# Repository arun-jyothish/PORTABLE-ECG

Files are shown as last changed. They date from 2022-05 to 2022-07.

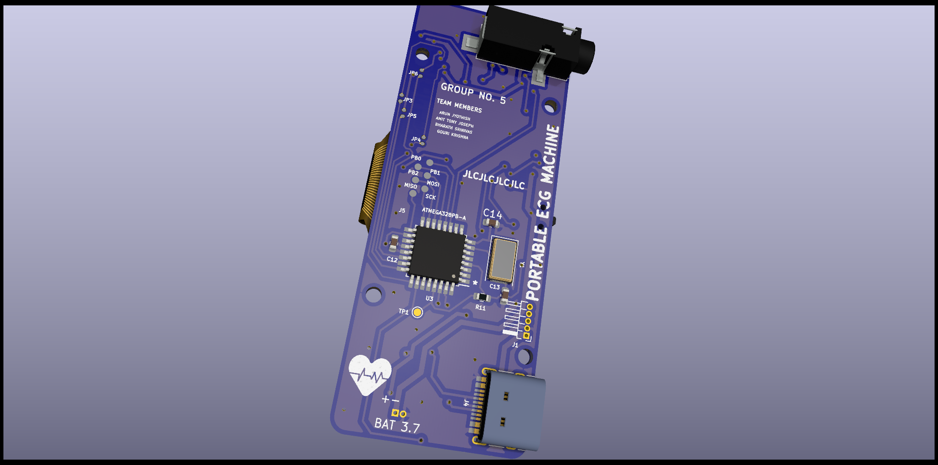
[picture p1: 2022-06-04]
KICAD FILES/imgs/P-ECG rev 3 kicad render 9.png

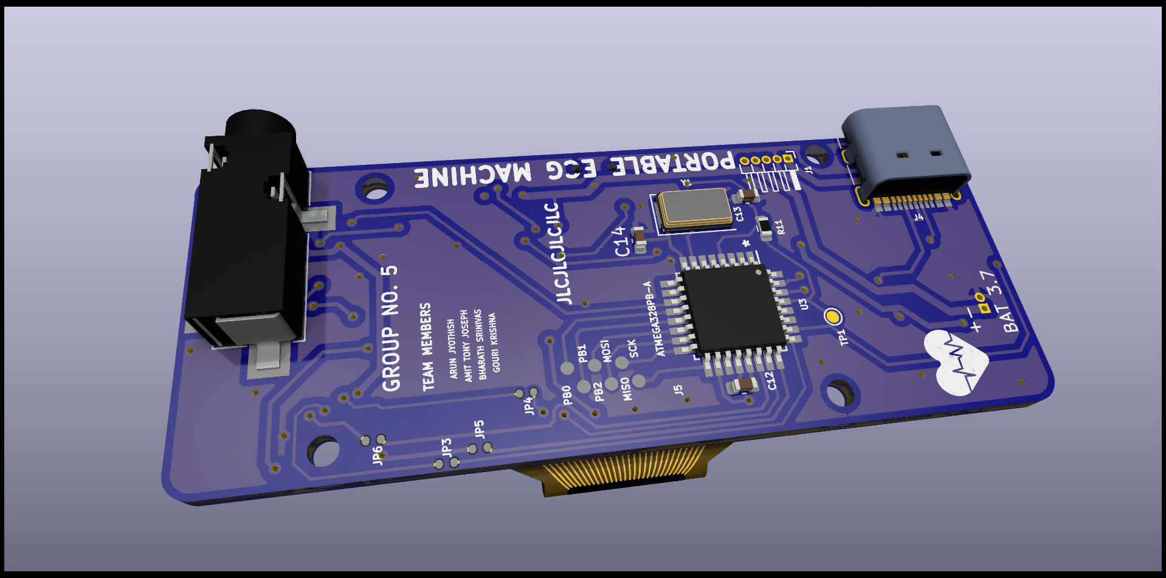
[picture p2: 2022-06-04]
KICAD FILES/imgs/P-ECG rev 3 kicad render 8.png

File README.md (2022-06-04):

# PORTABLE-ECG
A Handheld ECG Machine with Mobile phone and Laptop interface. Cardiac condition prediction using ML

[jump to README 2](src/README.md)

[variable link][var link]
LOCK

[var link]: https://GOOGLE.COM 

|part name|LCSC PART NO|LINK|
|-----|-----|----|
|OLED| 	C2890600|https://lcsc.com/product-detail/span-style-background-color-ff0-OLED-span-Displays-Modules_Shenzhen-Allvision-Tech-N096-2864TMBEG0-H30_C2890600.html|
|RESISTOR|
|CAPACITOR|
|TYPEC CONN|
hello world
<br>

[][Contributors-url]

<br>

f3d render 1 

## P-ECG MACHINE

In the prediction feature, patient's ECG signal is compared with various cardio gram.
as the processing result the machine filter out many heart disease and predicts the most probable disease that should affect the person's life'

## BLOCK DIAGRAM
~~~mermaid

graph TD
 
    UART-->PWR
    PWR[USB PORT]-->CHR[CHARGING CIRCUIT]
    CHR-->BAT[BATTERY 3.7 LI-ION]
    RGL[POWER REGULATOR]-.->|3.3 VOLT|OLED[OLED 128*64]
    CHR-->RGL
    BAT-->RGL
    RGL-.->|3.7 VOLT|UC 
    UC{MICROCONTROLLER}-->OLED
   
    UC-->UART[USB TO TTL CONVERTER]
    PWR-.->EXT[COMPUTER]
    PWR-.->EXT2[MOBILE]
    probe[/PROBE/]-->|DATA|INS
    RGL-.->INS
    RA((RA))-->probe
    RL((RL))-->probe
    LA((LA))-->probe
    INS[INSTRUMENTATION AMPLIFIER] --->|ANALOG DATA| UC
~~~

~~~mermaid
graph TD 

   I((IDEATION)) --> Q[PREPARE FAQ] 
    I --> D[CONSTRAINTS IN NEW IMPLEMENTATION]
    D-->M[ MEASURES TAKEN ]
    EX[IDENTIFYING EXISTING TECHNOLOGY]-->I
    FL[IDENTIFYING LIMITATIONS]-->I
    
~~~
~~~mermaid
graph TD
    H[COMPONENTS SELECTION]-->SCH[PREPARE SCHEMATICS]
    SCH-->PCB[DESIGN PCB LAYOUT]
   DSN[CHASY DESIGN]-->TST[TESTING STAGE]
    TST-.->|FAIL|SCH
    TST==>|SUCCESS|FINAL((PRODUCT))
    PCB-->DSN

~~~
[contributors-shield]: https://img.shields.io/github/contributors/Arun-jyothish/PORTABLE-ECG.svg?style=for-the-badge
[Contributors-url]:https://github.com/Arun-jyothish/PORTABLE-ECG/network/members

~~~mermaid

~~~

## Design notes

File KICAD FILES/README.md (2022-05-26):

# PORTABLE ECG MACHINE

According to current statistics, over 1.6 million people die in India due to a lack of access to
health care. Most of these cases occur in rural areas of the developing nations including India.<br>
Difficulty in accessing immediate health care is important for the proper treatment and recovery
of many diseases.
<br>
Heart diseases come under a category of conditions that need to be detected early for proper
recovery and treatment.

**An Electrocardiogram (ECG)** is a simple test that can be used to detect
the heart’s rhythm and electrical activity, thereby diagnosing conditions that affect the heart.

 <br>
It
can be used to investigate the symptoms of possible heart disease including chest pain,
palpitations, dizziness, shortness of breath, etc... which may point toward any heart condition
including 

<br>

* tachycardia
* bradycardia
* and heart attack.

<br>
There are many high-grade types of equipment in hospitals to carry out ECGs on patients. But in
many cases, the time taken to reach a hospital might be the fate that decides life or death. <br>There
are many places in the world where people are unable to access healthcare services quickly. <br>In
such cases, mainly in rural areas, a portable handheld device to carry out resting ECG can be
useful in detecting a heart condition.

<br>

### COMPONENTS USED

|HARDWARE|SOFTWARE|CHASE|
|--------|--------|-----|
|INSTRUMENTATION AMPLIFIER|STM32 CUBE IDE| PLA|

````mermaid
graph TD 
   I((IDEATION)) --> Q[PREPARE FAQ] 
    I --> D[CONSTRAINTS IN NEW IMPLEMENTATION]
    D-->M[ MEASURES TAKEN ]
    EX[IDENTIFYING EXISTING TECHNOLOGY]-->I
    FL[IDENTIFYING LIMITATIONS]-->I

````

--------

## HARDWARE IMPLEMENTATION STEPS

````mermaid
graph TD
    H[COMPONENTS SELECTION]-->SCH[PREPARE SCHEMATICS]
    SCH-->PCB[DESIGN PCB LAYOUT]
   DSN[CHASY DESIGN]-->TST[TESTING STAGE]
    TST-.->|FAIL|SCH
    TST==>|SUCCESS|FINAL((PRODUCT))
    PCB-->DSN
````

## SYSTEM SPECIFICATION

* HEART RATE MEASUREMENT
* SPO2 MEASURE
* PLOT/STORE ECG IN MOBILE DEVICES
* DETECT CARDIAC VARIATION DUE TO COMMONLY KNOWN HEART DISEASE

## GANT CHART

~~~mermaid

~~~

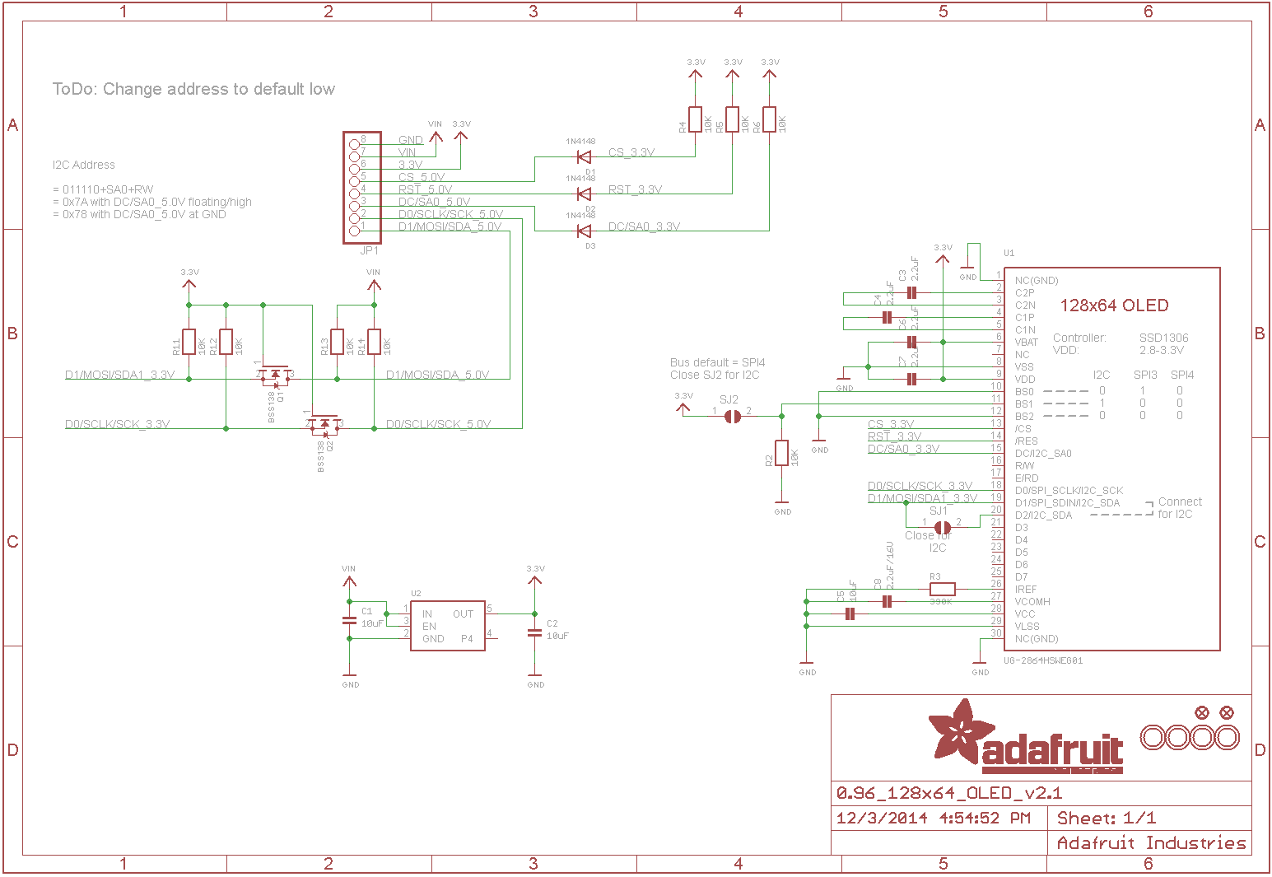
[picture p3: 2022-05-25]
imgs/oled_adafruit_0.94inch_12864_v2.1_schematics.png.png

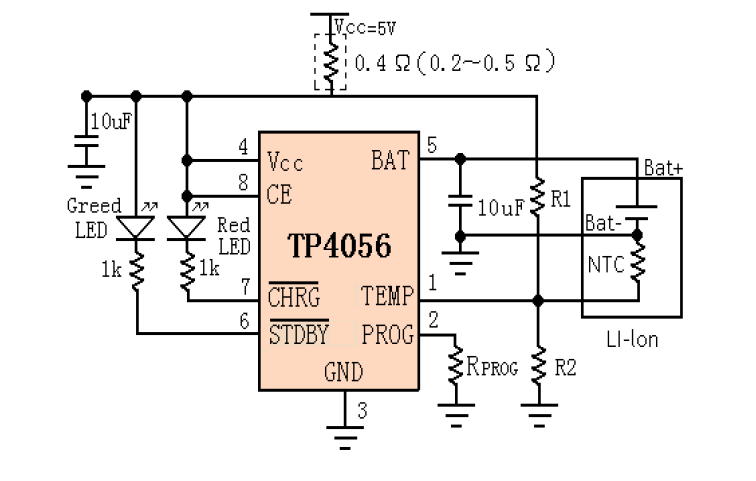
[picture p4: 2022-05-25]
imgs/TP4056 SCHEMATICS.png

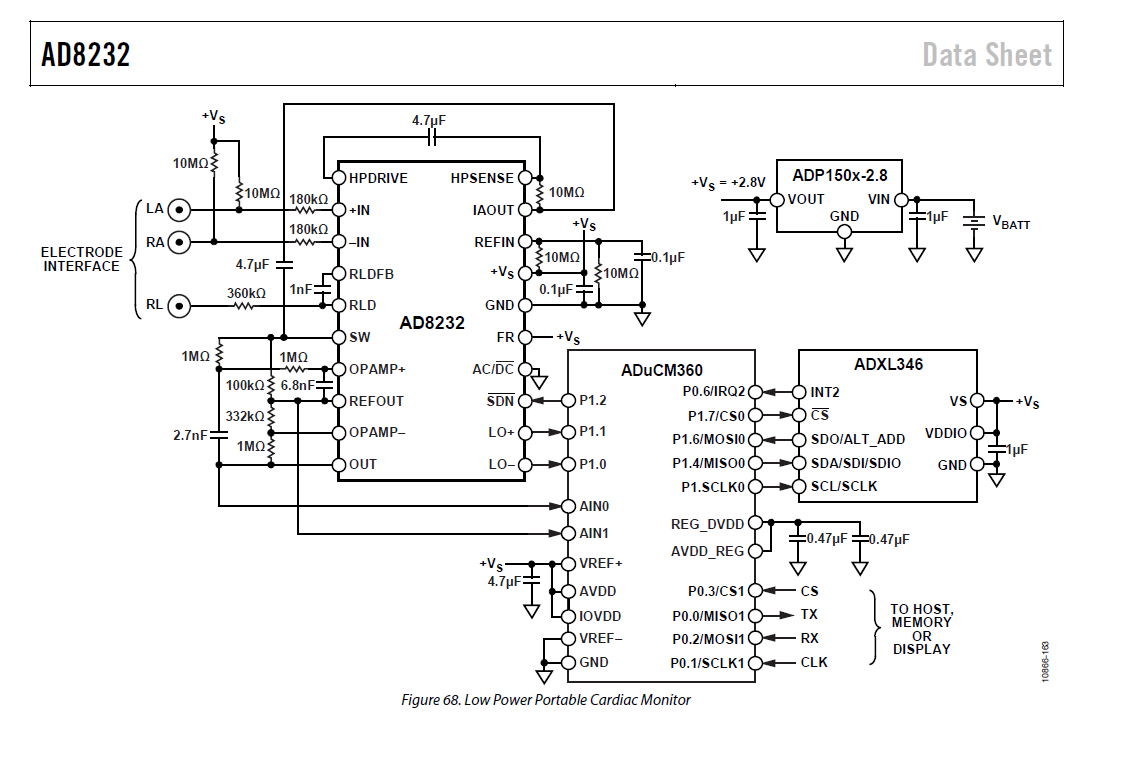
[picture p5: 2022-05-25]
imgs/AD8232 REF SCHEMATICS.png

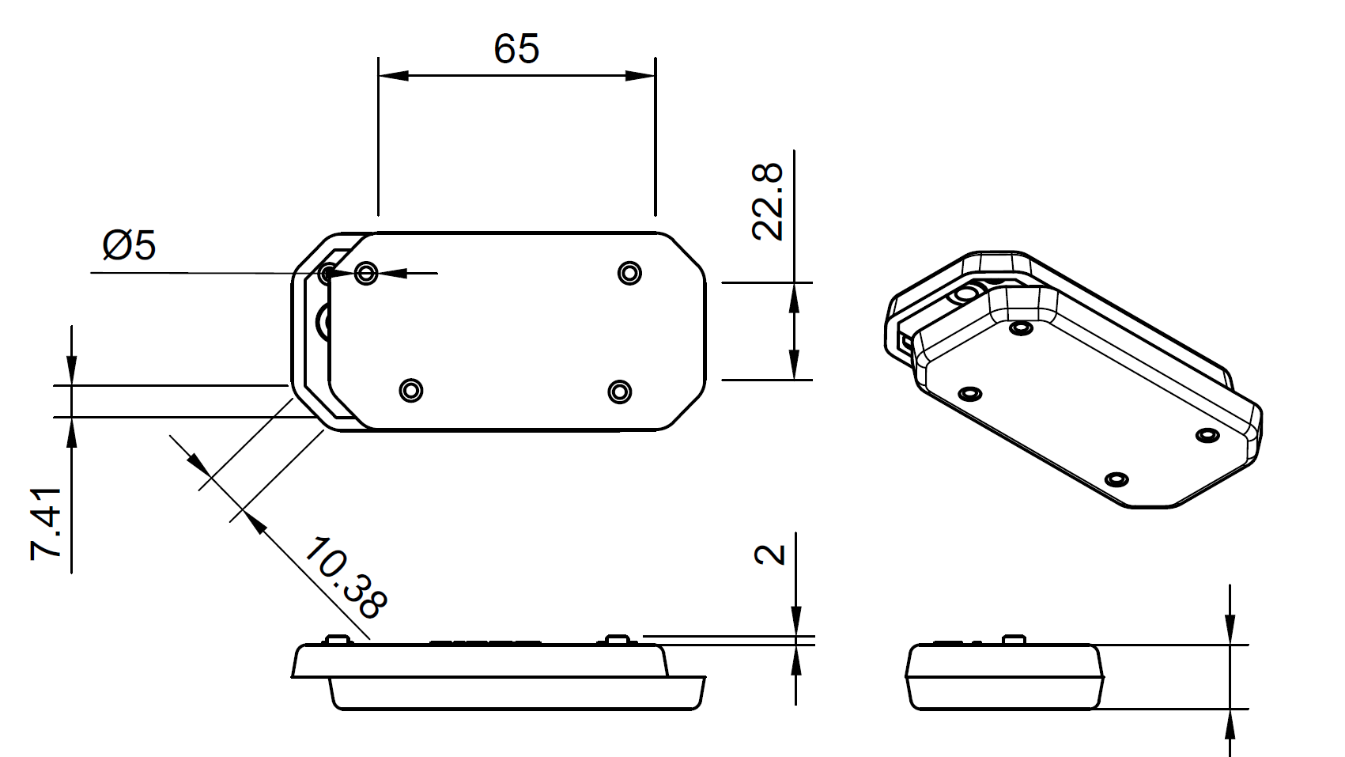
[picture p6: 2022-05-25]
imgs/DRAWING ENCLOSURE.png

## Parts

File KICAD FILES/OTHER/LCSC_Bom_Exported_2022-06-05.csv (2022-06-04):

LCSC Part Number | Package | Value | Quoted Manufacturer | Quoted LCSC Part Number | Quantity | Unit Price | Order Price | Quantity Available | Min\Mult Order Qty | RoHS | Part Match Confidence
C2204347 | Capacitor_SMD:C_0603_1608Metric | 4.7uf | AVX | C2204347 | 1 |  | 0.01 |  | 1\1 | yes | 100%
C2184695 | Capacitor_SMD:C_0603_1608Metric | 10p | KEMET | C2184695 | 1 |  | 0.01 |  | 1\1 | yes | 100%
C100040 | Capacitor_SMD:C_0603_1608Metric | 1nf | YAGEO | C100040 | 100 | 0.0026 | 0.26 | 8197500 | 100\100 | yes | 100%
C107085 | Capacitor_SMD:C_0603_1608Metric | 2.7nf | YAGEO | C107085 | 100 | 0.0036 | 0.36 | 1100 | 100\100 | yes | 100%
C2185892 | Capacitor_SMD:C_0603_1608Metric | 6.8nf | Vishay Intertech | C2185892 | 1 |  | 0.01 |  | 1\1 | yes | 100%
C2237744 | Capacitor_SMD:C_0603_1608Metric | .1uf | AVX | C2237744 | 1 |  | 0 |  | 1\1 | yes | 100%
C2168630 | Capacitor_SMD:C_0603_1608Metric | 1uf | KEMET | C2168630 | 1 |  | 0.01 |  | 1\1 | yes | 100%
C2858007 | Capacitor_SMD:C_0603_1608Metric | 2.2uf | Kyocera | C2858007 | 1 |  | 0.01 |  | 1\1 | yes | 100%
C2167337 | Capacitor_SMD:C_0603_1608Metric | 10uf | AVX | C2167337 | 1 |  | 0.01 |  | 1\1 | yes | 100%
C109002 | Diode_SMD:D_0603_1608Metric | 4148 | LIZ Elec | C109002 | 20 |  | 0.48 |  | 20\20 | yes | 100%
C143772 | Diode_SMD:D_0603_1608Metric | D_Schottky | AVX | C143772 | 5 | 0.1088 | 0.54 | 2740 | 5\5 | yes | 100%
C221856 | tactile switch:SW_PTS525SM15SMTR2LFS | PTS525SM15SMTR2LFS | C&K | C221856 | 1 | 0.1383 | 0.14 | 6655 | 1\1 | yes | 100%
C2917809 | LED_SMD:LED_0603_1608Metric | LED GREEN | PARALIGHT | C2917809 | 10 | 0.045 | 0.45 | 3760 | 10\10 | yes | 100%
C652575 | KiCad:QFN50P400X400X80-21N-D | AD8232ACPZ | Analog Devices | C652575 | 1 |  | 3.29 |  | 1\1 | yes | 100%
C2939151 | Connector_Audio:Jack_3.5mm_CUI_SJ-3524-SMT_Horizontal | ECG PROBE | HOOYA | C2939151 | 1 | 0.1687 | 0.17 | 494 | 1\1 | yes | 100%
C2927026 | Connector_USB:USB_C_Receptacle_HRO_TYPE-C-31-M-12 | USB_C_Receptacle_USB2.0 | DEALON | C2927026 | 10 | 0.046 | 0.46 | 6380 | 10\10 | yes | 100%
C549757 | Package_TO_SOT_SMD:SOT-23 | BSS138 | Nexperia | C549757 | 1 |  | 0.3 |  | 1\1 | yes | 100%
C2907166 | Resistor_SMD:R_0603_1608Metric | 4.7k | FOJAN | C2907166 | 100 | 0.0009 | 0.09 | 95000 | 100\100 | yes | 100%
C2907090 | Resistor_SMD:R_0603_1608Metric | 180k | FOJAN | C2907090 | 100 | 0.0009 | 0.09 | 32000 | 100\100 | yes | 100%
C2907090 | Resistor_SMD:R_0603_1608Metric | 360k | FOJAN | C2907090 | 100 | 0.0009 | 0.09 | 32000 | 100\100 | yes | 100%
C2907115 | Resistor_SMD:R_0603_1608Metric | 1M | FOJAN | C2907115 | 100 | 0.001 | 0.1 | 34400 | 100\100 | yes | 100%
C2930027 | Resistor_SMD:R_0603_1608Metric | 10k | FOJAN | C2930027 | 100 | 0.0009 | 0.09 | 1457500 | 100\100 | yes | 100%
C2907151 | Resistor_SMD:R_0603_1608Metric | 330k | FOJAN | C2907151 | 100 | 0.001 | 0.1 | 56400 | 100\100 | yes | 100%
C328419 | Resistor_SMD:R_0603_1608Metric | 100k | Resistor.Today | C328419 | 10 | 0.073 | 0.73 | 25140 | 10\10 | yes | 100%
C2907088 | Resistor_SMD:R_0603_1608Metric | 0.4R | FOJAN | C2907088 | 100 | 0.0009 | 0.09 | 394400 | 100\100 | yes | 100%
C2913953 | Resistor_SMD:R_0603_1608Metric | 1k | SANYEAR | C2913953 | 20 | 0.0247 | 0.49 | 1100 | 20\20 | yes | 100%
C304747 | Resistor_SMD:R_0603_1608Metric | 390k | FH(Guangdong Fenghua Advanced Tech) | C304747 | 100 | 0.001 | 0.1 | 8100 | 100\100 | yes | 100%
C2907090 | Resistor_SMD:R_0603_1608Metric | 10M | FOJAN | C2907090 | 100 | 0.0009 | 0.09 | 32000 | 100\100 | yes | 100%
C2917808 | LED_SMD:LED_0603_1608Metric | LED RED | PARALIGHT | C2917808 | 10 | 0.045 | 0.45 | 2470 | 10\10 | yes | 100%
C2890358 | Button_Switch_SMD:SW_SPDT_PCM12 | SW_SPDT | G-Switch | C2890358 | 5 | 0.1077 | 0.54 | 20420 | 5\5 | yes | 100%
C6568 | CP2102-GM:QFN50P500X500X100-29N | CP2102-GM | SILICON LABS | C6568 | 1 | 2.6833 | 2.68 | 21873 | 1\1 | yes | 100%
C194192 | Package_QFP:TQFP-32_7x7mm_P0.8mm | ATmega328PB-A | Microchip Tech | C194192 | 1 |  | 2.88 |  | 1\1 | yes | 100%
C140319 | Package_TO_SOT_SMD:SOT-223 | LM3940IMP-3.3/NOPB | Texas Instruments | C140319 | 1 | 1.4084 | 1.41 | 1672 | 1\1 | yes | 100%
C725790 | tp4056 ftprnt:SOP127P600X175-9N | TP4056 | UMW(Youtai Semiconductor Co., Ltd.) | C725790 | 1 | 0.1348 | 0.13 | 23205 | 1\1 | yes | 100%
C2890600 | Display:OLED-128O064D | SSD1306 | Shenzhen Allvision Tech | C2890600 | 1 | 3.4696 | 3.47 | 53 | 1\1 | yes | 100%
C112972 | Crystal:Crystal_SMD_0603-2Pin_6.0x3.5mm | 16MHZ | Yangxing Tech | C112972 | 5 | 0.0904 | 0.45 | 13570 | 5\5 | yes | 100%

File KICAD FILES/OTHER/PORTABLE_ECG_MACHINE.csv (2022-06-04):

Comment | Designator | Footprint | LCSC
B-TEMP | B_TEMP1 | TestPoint:TestPoint_Pad_D1.0mm
4.7uf | C1,C15,C17,C24 | Capacitor_SMD:C_0603_1608Metric | C2204347
10p | C13,C14 | Capacitor_SMD:C_0603_1608Metric | C2184695
1nf | C16 | Capacitor_SMD:C_0603_1608Metric | C100040
2.7nf | C18 | Capacitor_SMD:C_0603_1608Metric | C107085
6.8nf | C19 | Capacitor_SMD:C_0603_1608Metric | C2185892
.1uf | C2,C8,C10,C11,C12,C22 | Capacitor_SMD:C_0603_1608Metric | C2237744
1uf | C3,C4,C5,C20,C21 | Capacitor_SMD:C_0603_1608Metric | C2168630
2.2uf | C6 | Capacitor_SMD:C_0603_1608Metric | C2858007
10uf | C7,C23 | Capacitor_SMD:C_0603_1608Metric | C2167337
D+ | D+1 | TestPoint:TestPoint_Pad_D1.0mm
D- | D-1 | TestPoint:TestPoint_Pad_D1.0mm
4148 | D1 | Diode_SMD:D_0603_1608Metric | C109002
D_Schottky | D2,D3 | Diode_SMD:D_0603_1608Metric | C143772
PTS525SM15SMTR2LFS | DRIVE1,SELECT1 | tactile switch:SW_PTS525SM15SMTR2LFS | C221856
LED GREEN | GREEN1 | LED_SMD:LED_0603_1608Metric | C2917809
AD8232ACPZ | IC1 | KiCad:QFN50P400X400X80-21N-D | C652575
UART | J1 | Connector_PinHeader_1.00mm:PinHeader_1x05_P1.00mm_Horizontal
ECG PROBE | J2 | Connector_Audio:Jack_3.5mm_CUI_SJ-3524-SMT_Horizontal | C2939151
Li-Ion 3.7 CONN | J3 | Connector_PinHeader_1.00mm:PinHeader_1x02_P1.00mm_Horizontal
USB_C_Receptacle_USB2.0 | J4 | Connector_USB:USB_C_Receptacle_HRO_TYPE-C-31-M-12 | C2927026
Conn_01x06_Male | J5 | TEST_POINT_MATRIX_6-PIN:6PIN_CONN
SolderJumper_3_Open | JP1,JP2 | TEST_POINT_MATRIX_6-PIN:3_PIN_SOLDER_JUMPER_SMD
LDO+ | JP3,JP6 | TEST_POINT_MATRIX_6-PIN:2_PIN_SMD_SOLDER_JUMPER
LDO- | JP4 | TEST_POINT_MATRIX_6-PIN:2_PIN_SMD_SOLDER_JUMPER
OUT | JP5 | TEST_POINT_MATRIX_6-PIN:2_PIN_SMD_SOLDER_JUMPER
REF | JP7 | TEST_POINT_MATRIX_6-PIN:2_PIN_SMD_SOLDER_JUMPER
RST | JP8 | TEST_POINT_MATRIX_6-PIN:2_PIN_SMD_SOLDER_JUMPER
LA | LA1 | TestPoint:TestPoint_Pad_D1.0mm
BSS138 | Q1,Q2 | Package_TO_SOT_SMD:SOT-23 | C549757
4.7k | R1 | Resistor_SMD:R_0603_1608Metric | C2907166
180k | R14,R15 | Resistor_SMD:R_0603_1608Metric | C2907090
360k | R16 | Resistor_SMD:R_0603_1608Metric | C2907090
1M | R19 | Resistor_SMD:R_0603_1608Metric | C2907115
10k | R2,R3,R5,R6,R7,R11 | Resistor_SMD:R_0603_1608Metric | C2930027
330k | R20 | Resistor_SMD:R_0603_1608Metric | C2907151
100k | R21 | Resistor_SMD:R_0603_1608Metric | C328419
0.4R | R22 | Resistor_SMD:R_0603_1608Metric | C2907088
1k | R23,R24 | Resistor_SMD:R_0603_1608Metric | C2913953
R_Small_US | R25,R26 | Resistor_SMD:R_0603_1608Metric
R_prog | R27 | Resistor_SMD:R_0603_1608Metric
390k | R4 | Resistor_SMD:R_0603_1608Metric | C304747
10M | R8,R9,R10,R12,R13,R17,R18 | Resistor_SMD:R_0603_1608Metric | C2907090
RA | RA1 | TestPoint:TestPoint_Pad_D1.0mm
LED RED | RED1 | LED_SMD:LED_0603_1608Metric | C2917808
RL | RL1 | TestPoint:TestPoint_Pad_D1.0mm
0-RST | RST_CP1 | TestPoint:TestPoint_Pad_D1.0mm
SW_SPDT | SW1 | Button_Switch_SMD:SW_SPDT_PCM12 | C2890358
AT_RST# | TP1 | TestPoint:TestPoint_Pad_D1.0mm
CP2102-GM | U2 | CP2102-GM:QFN50P500X500X100-29N | C6568
ATmega328PB-A | U3 | Package_QFP:TQFP-32_7x7mm_P0.8mm | C194192
LM3940IMP-3.3/NOPB | U4 | Package_TO_SOT_SMD:SOT-223 | C140319
TP4056 | U5 | tp4056 ftprnt:SOP127P600X175-9N | C725790
SSD1306 | U6 | Display:OLED-128O064D | C2890600
16MHZ | Y1 | Crystal:Crystal_SMD_0603-2Pin_6.0x3.5mm | C112972

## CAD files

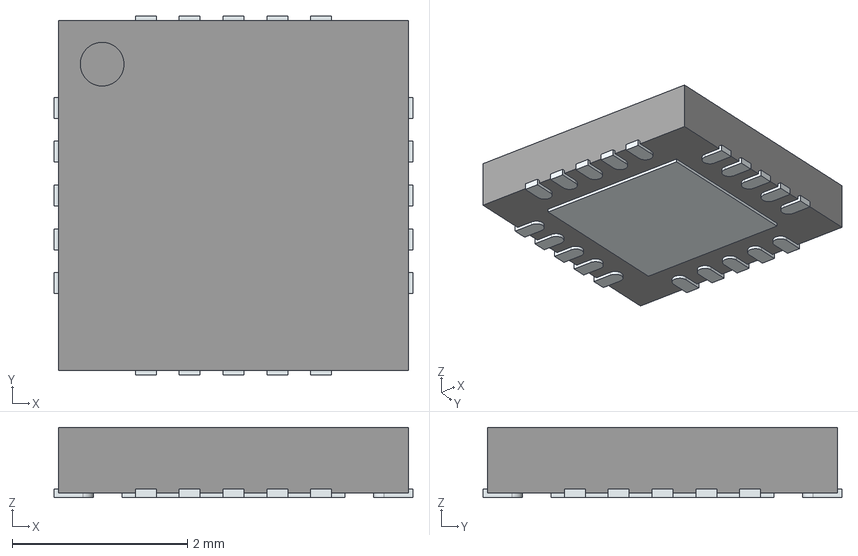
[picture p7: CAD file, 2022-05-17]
KICAD FILES/models/AD8232ACPZ/3D/AD8232ACPZ.stp
4.10 x 4.10 x 0.8 mm
ThermalPin
PinsArrayLR
PinsArrayTB

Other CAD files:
KICAD FILES/models/AD8232ACPZ/3D/AD8232ACPZ.stl

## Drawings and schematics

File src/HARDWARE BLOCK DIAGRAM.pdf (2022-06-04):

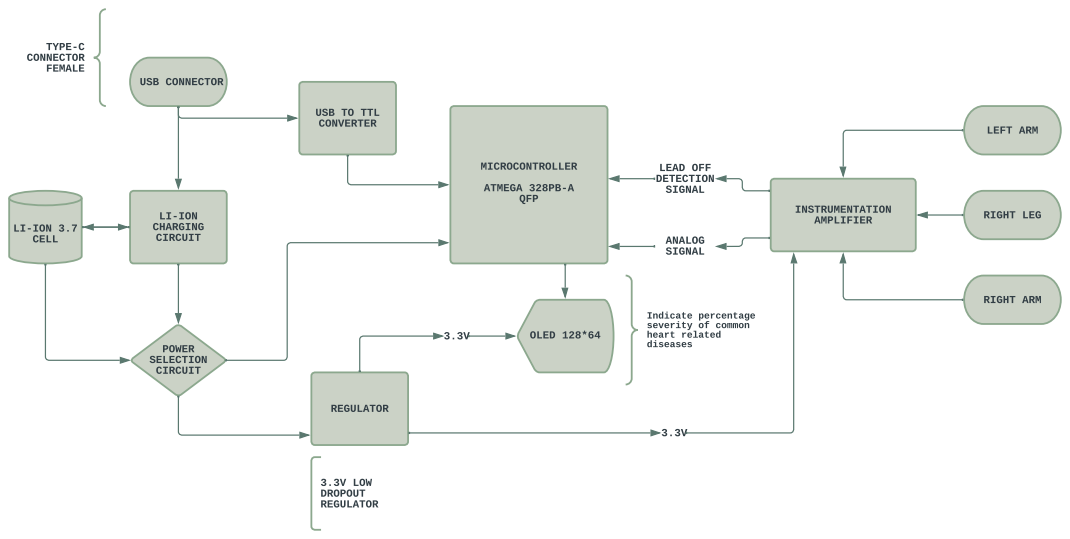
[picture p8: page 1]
MI CROCONTROLLER; ATMEGA 328PB- A QFP; USB CONNECTOR; LI - I ON CHARGI NG CI RCUI T; POWER SELECTI ON CI RCUI T; LI - I ON 3. 7 CELL; OLED 128* 64; LEFT ARM; REGULATOR; TYPE- C CONNECTOR FEMALE; 3. 3V LOW DROPOUT REGULATOR; ANALOG SI GNAL; LEAD OFF DETECTI ON SI GNAL

USB TO TTL
CONVERTER

I NSTRUMENTATI ON
AMPLI FI ER

RI GHT LEG

RI GHT ARM

I ndi cat e per cent age
sever i t y of common
hear t r el at ed
di seases

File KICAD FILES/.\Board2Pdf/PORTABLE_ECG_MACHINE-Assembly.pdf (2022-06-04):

13.2080 mm

1 | 2 | 3 | 4

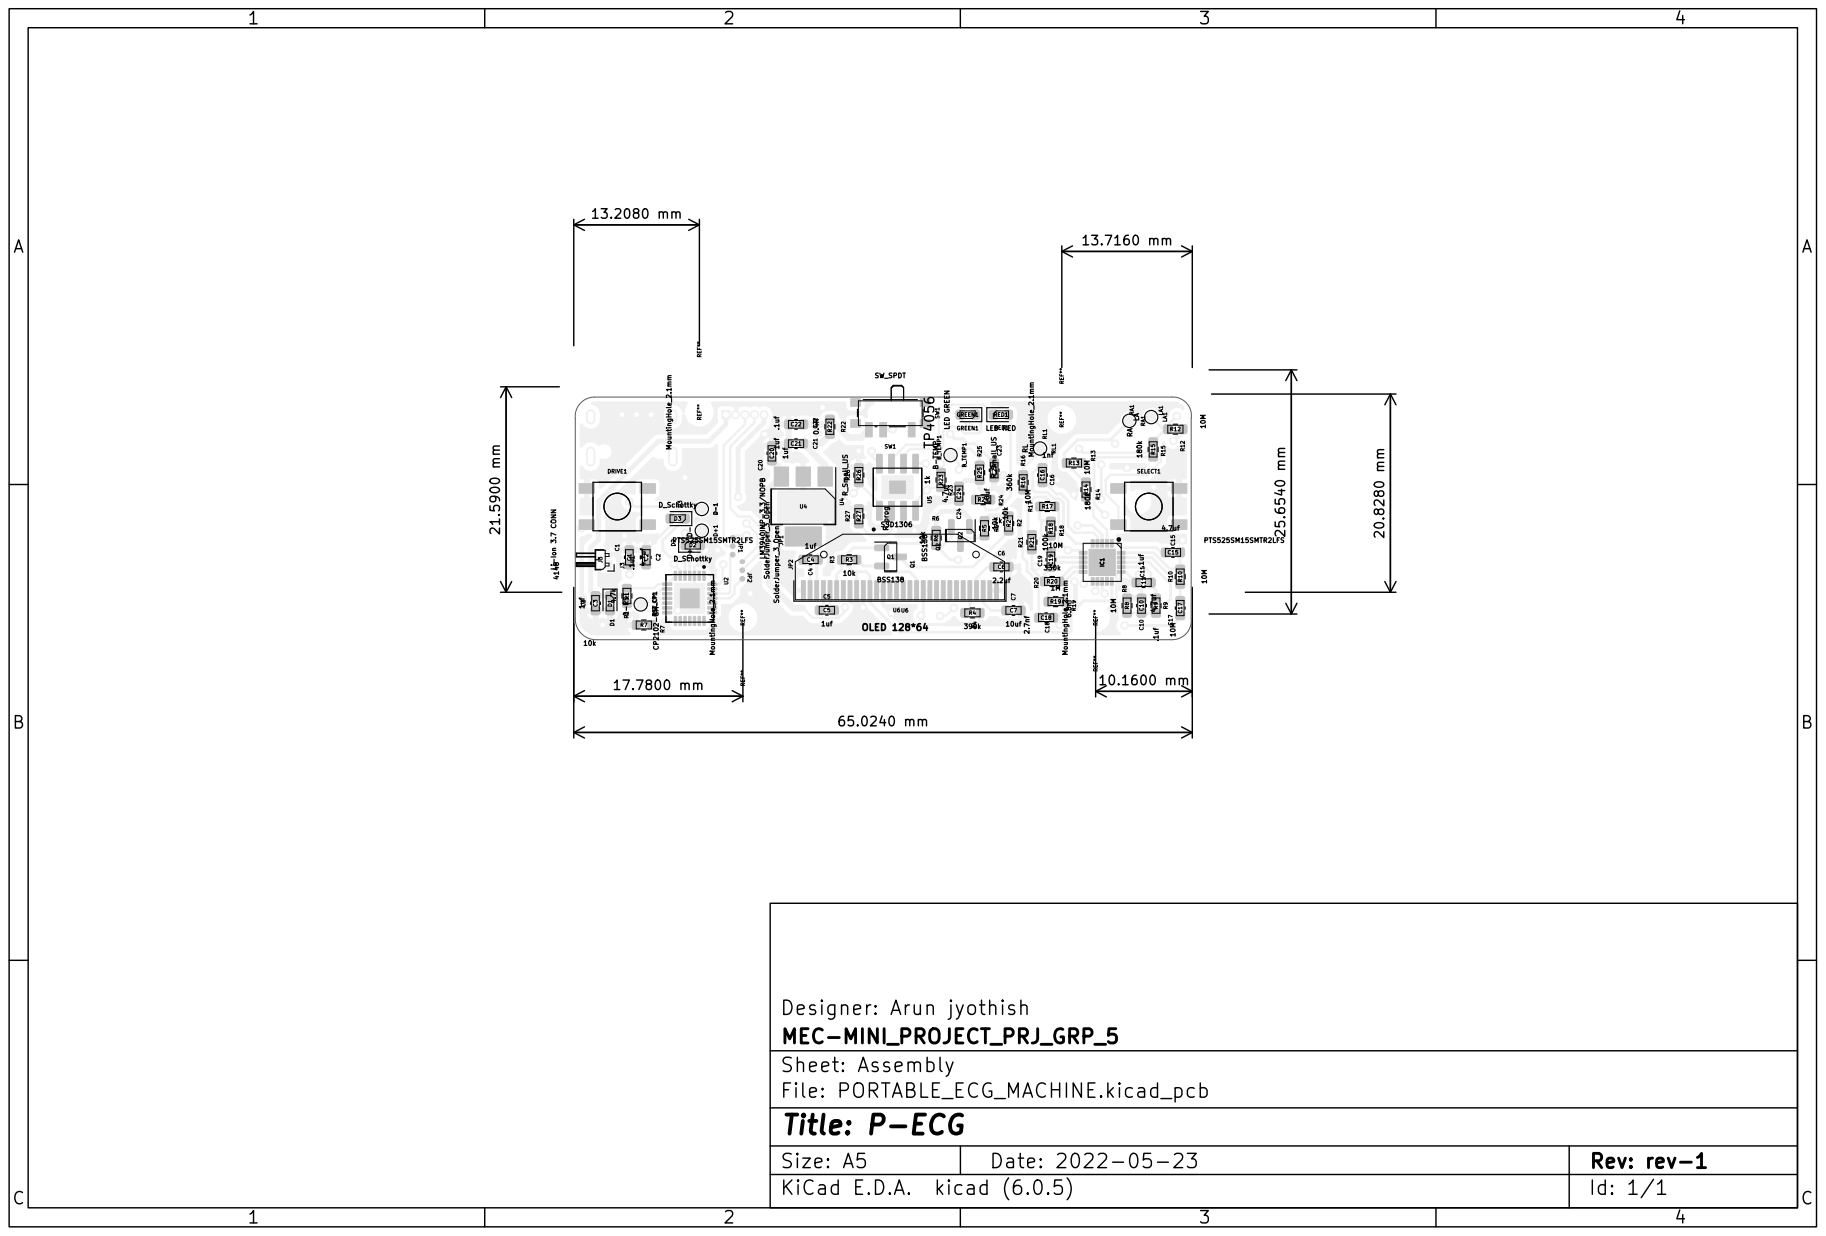
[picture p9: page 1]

J2 | TP1 1 | 2 | 3 | 4

A

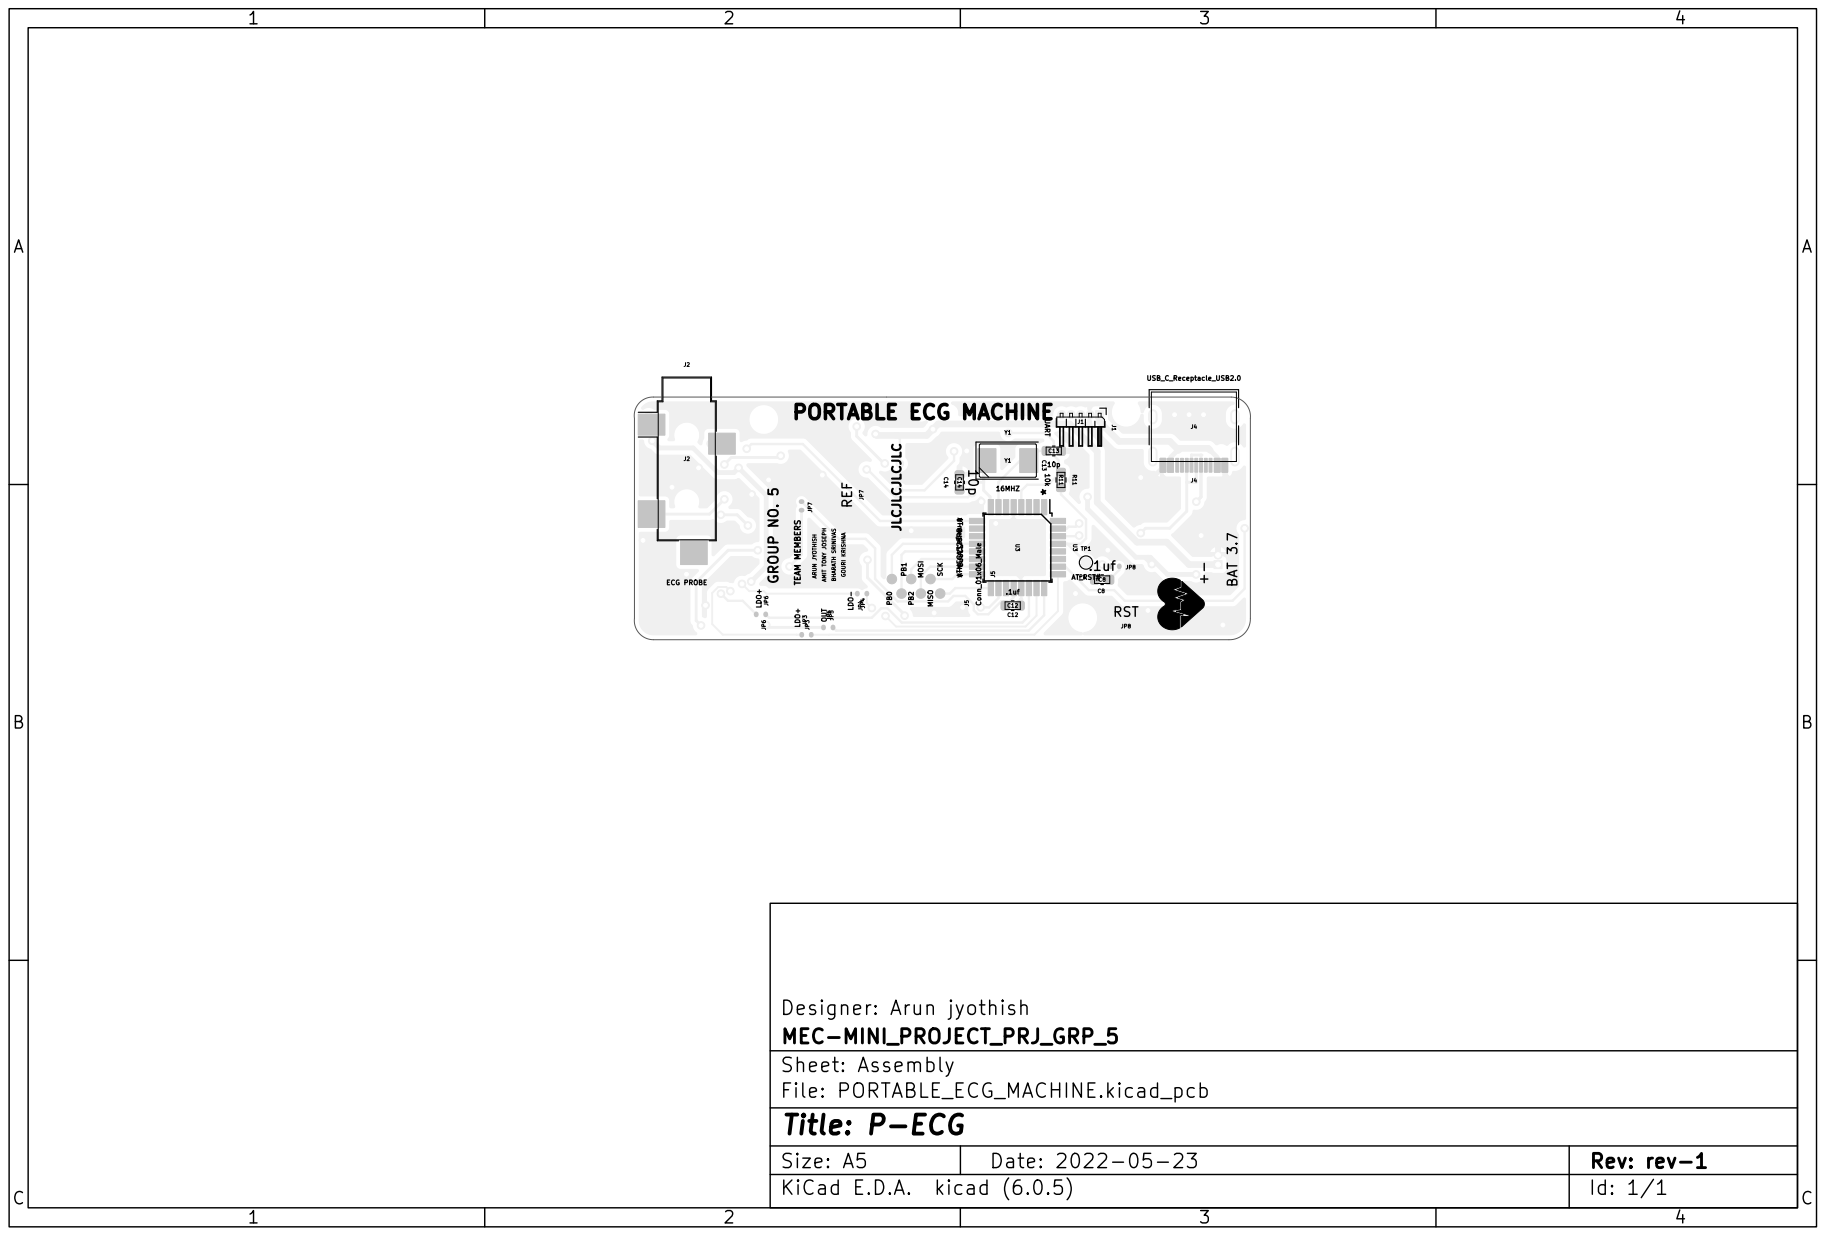
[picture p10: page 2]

PB0 GROUP NO. 5 + PB2 JLCJLCJLCJLC TEAM MEMBERS BAT 3.7 GOURI KRISHNA ATMEGA328PB-A - ARUN JYOTHISH MOSI AMIT TONY JOSEPH PB1 SCK BHARATH SRINIVAS PORTABLE ECG MACHINE MISO

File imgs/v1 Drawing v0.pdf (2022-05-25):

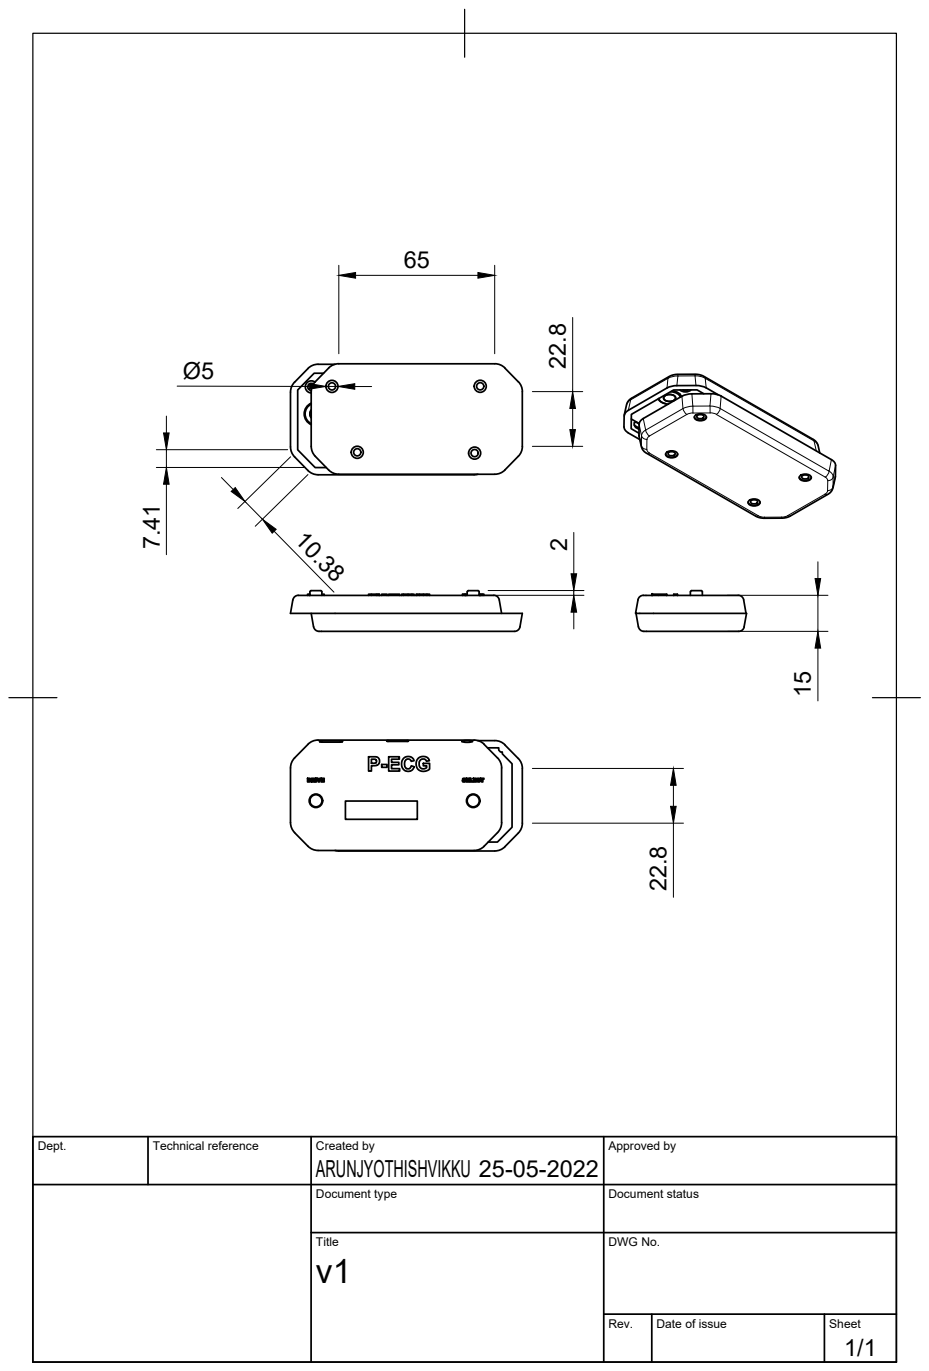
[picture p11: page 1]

Dept. | Technical reference | Created by ARUNJYOTHISHVIKKU 25-05-2022 | Approved by

Document type | Document status

Title v1 | DWG No.

Rev. | Date of issue | Sheet 1/1

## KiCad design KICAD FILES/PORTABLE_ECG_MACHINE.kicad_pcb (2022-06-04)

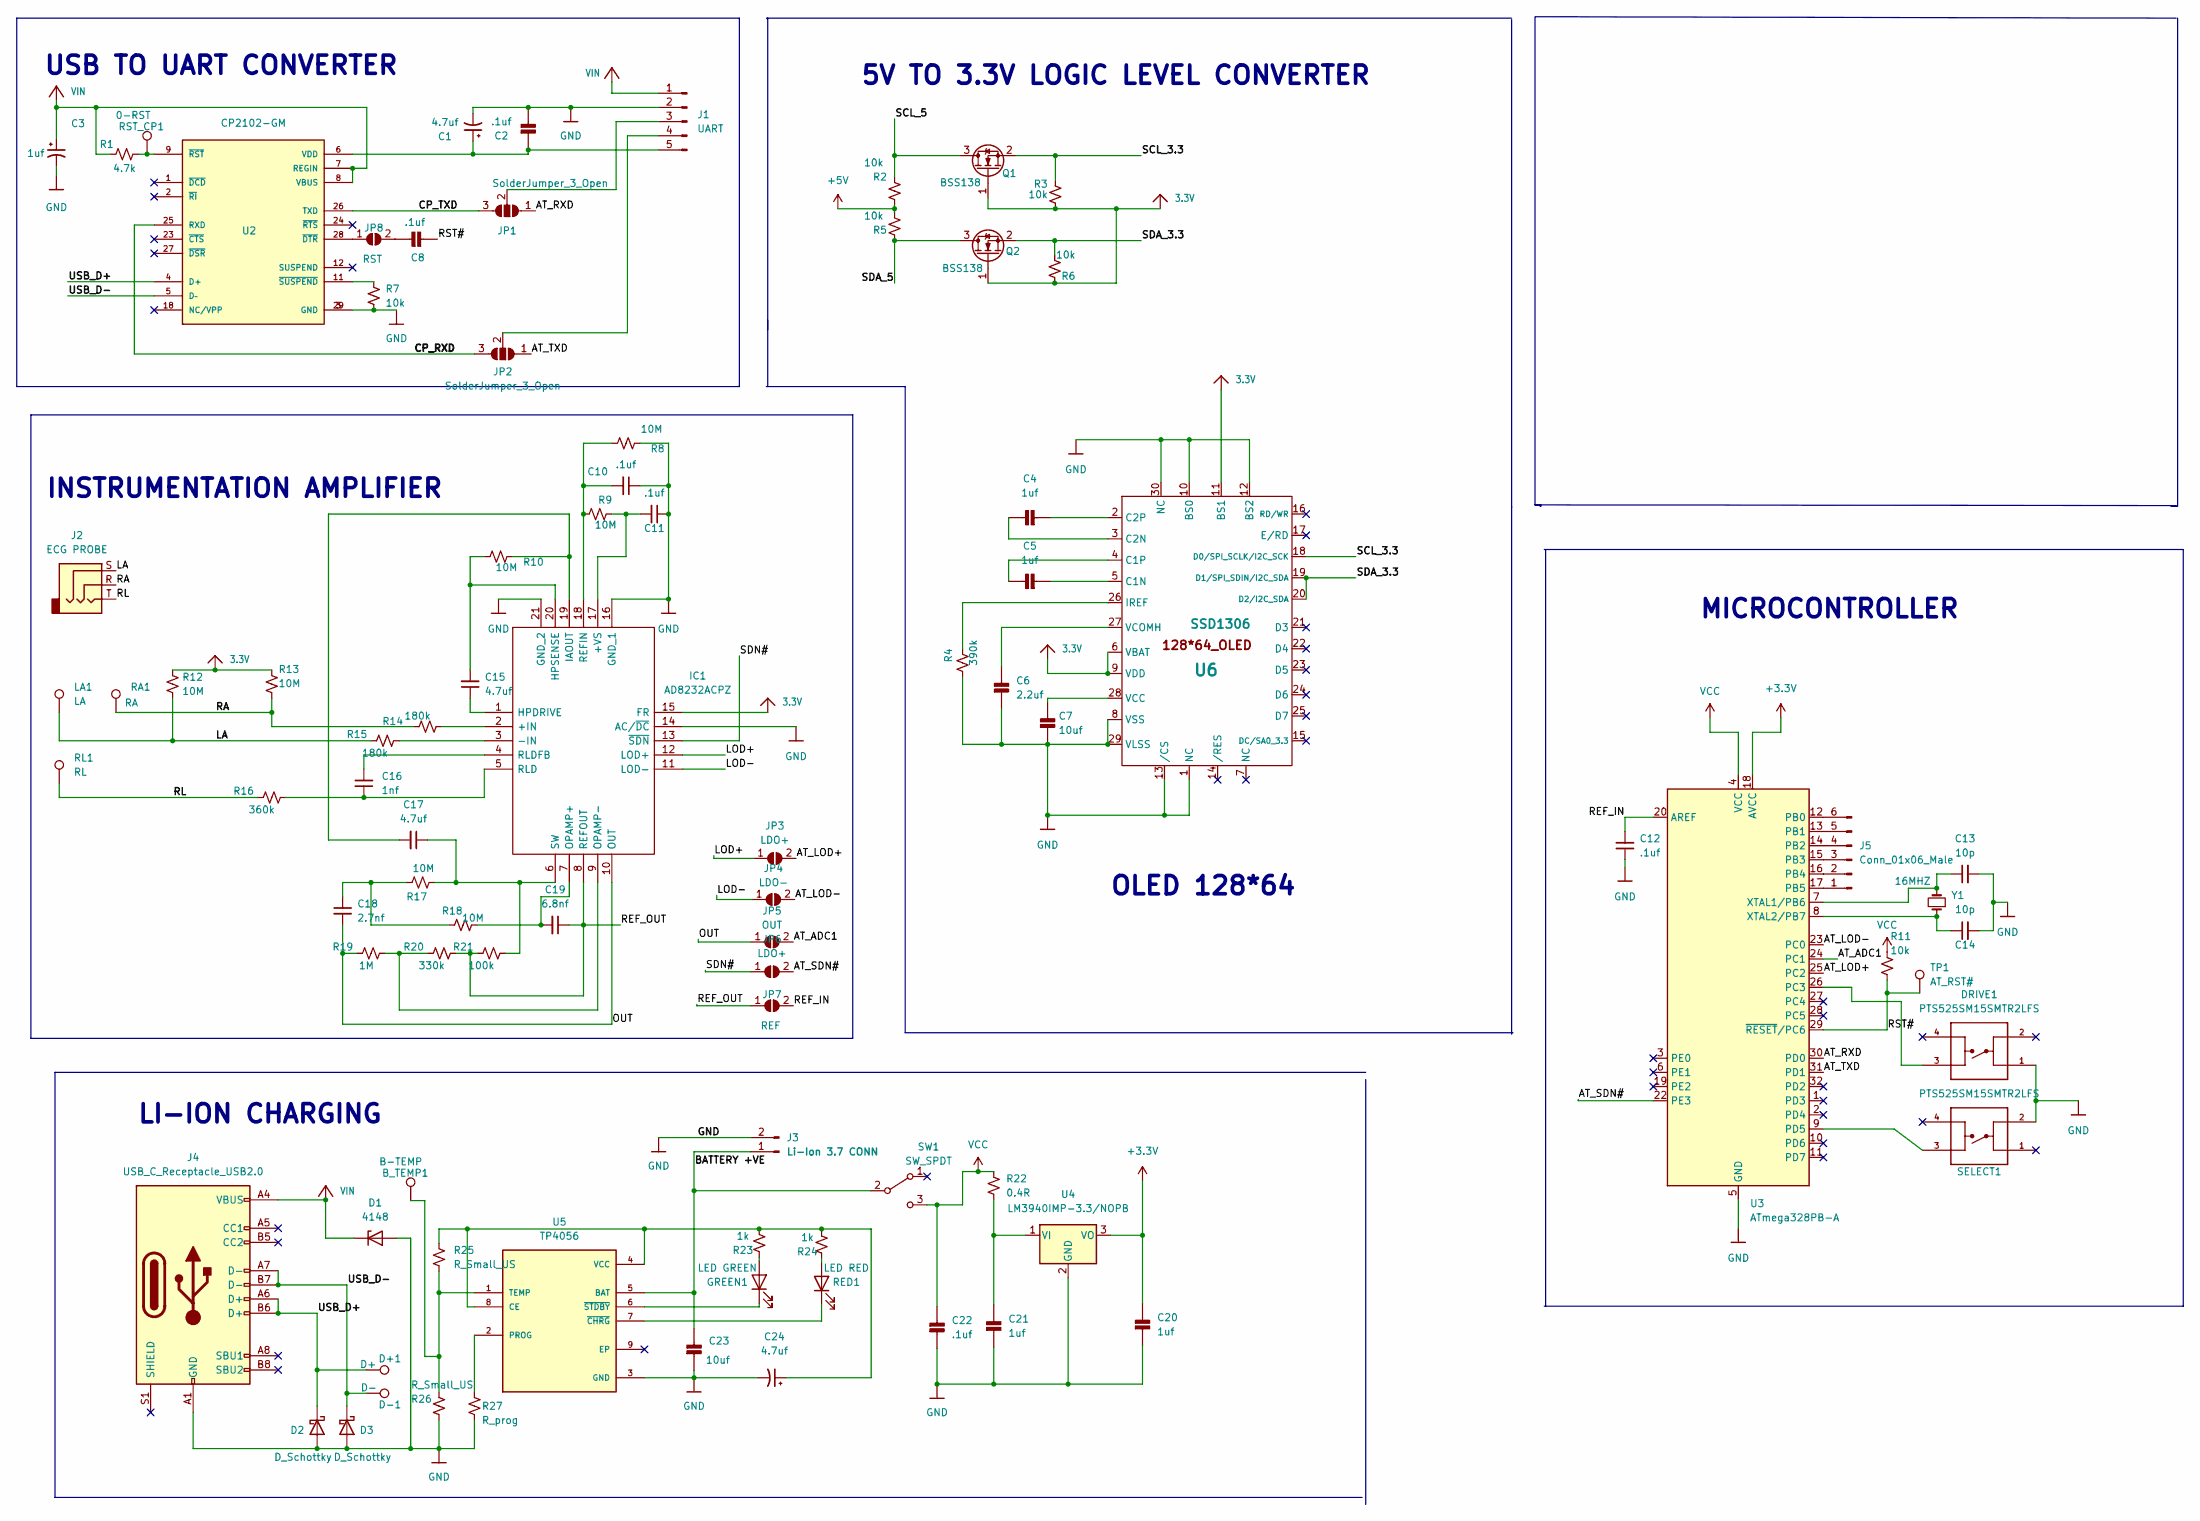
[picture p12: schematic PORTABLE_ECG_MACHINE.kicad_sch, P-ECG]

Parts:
B_TEMP1: B-TEMP; TestPoint_Pad_D1.0mm
C1, C15, C17, C24: 4.7uf; C_0603_1608Metric; JLC PCB PART NUMBER C2204347
C2, C8, C10, C11, C12, C22: .1uf; C_0603_1608Metric; JLC PCB PART NUMBER C2237744
C3, C4, C5, C20, C21: 1uf; C_0603_1608Metric; JLC PCB PART NUMBER C2168630
C6: 2.2uf; C_0603_1608Metric; JLC PCB PART NUMBER C2858007
C7, C23: 10uf; C_0603_1608Metric; JLC PCB PART NUMBER C2167337
C13, C14: 10p; C_0603_1608Metric; JLC PCB PART NUMBER C2184695
C16: 1nf; C_0603_1608Metric; JLC PCB PART NUMBER C100040
C18: 2.7nf; C_0603_1608Metric; JLC PCB PART NUMBER C107085
C19: 6.8nf; C_0603_1608Metric; JLC PCB PART NUMBER C2185892
D1: 4148; D_0603_1608Metric; JLC PCB PART NUMBER C109002
D2, D3: D_Schottky; D_0603_1608Metric; JLC PCB PART NUMBER C143772
D+1: D+; TestPoint_Pad_D1.0mm
D-1: D-; TestPoint_Pad_D1.0mm
DRIVE1: PTS525SM15SMTR2LFS; SW_PTS525SM15SMTR2LFS; PARTREV NA; JLC PCB PART NUMBER C221856
GREEN1: LED GREEN; LED_0603_1608Metric; JLC PCB PART NUMBER C2917809
IC1: AD8232ACPZ; QFN50P400X400X80-21N-D; Manufacturer_Part_Number AD8232ACPZ; Mouser Part Number N/A
J1: UART; PinHeader_1x05_P1.00mm_Horizontal
J2: ECG PROBE; Jack_3.5mm_CUI_SJ-3524-SMT_Horizontal; JLC PCB PART NUMBER C2939151
J3: Li-Ion 3.7 CONN; PinHeader_1x02_P1.00mm_Horizontal
J4: USB_C_Receptacle_USB2.0; USB_C_Receptacle_HRO_TYPE-C-31-M-12; JLC PCB PART NUMBER C2927026
J5: Conn_01x06_Male; 6PIN_CONN
JP1, JP2: SolderJumper_3_Open; 3_PIN_SOLDER_JUMPER_SMD
JP3, JP6: LDO+; 2_PIN_SMD_SOLDER_JUMPER
JP4: LDO-; 2_PIN_SMD_SOLDER_JUMPER
JP5: OUT; 2_PIN_SMD_SOLDER_JUMPER
JP7: REF; 2_PIN_SMD_SOLDER_JUMPER
JP8: RST; 2_PIN_SMD_SOLDER_JUMPER
LA1: LA; TestPoint_Pad_D1.0mm
Q1, Q2: BSS138; SOT-23; JLC PCB PART NUMBER C549757
R1: 4.7k; R_0603_1608Metric; JLC PCB PART NUMBER C2907166
R2, R3, R5, R6, R7, R11: 10k; R_0603_1608Metric; JLC PCB PART NUMBER C2930027
R4: 390k; R_0603_1608Metric; JLC PCB PART NUMBER C304747
R8, R9, R10, R12, R13, R17, R18: 10M; R_0603_1608Metric; JLC PCB PART NUMBER C2907090
R14, R15: 180k; R_0603_1608Metric; JLC PCB PART NUMBER C2907090
R16: 360k; R_0603_1608Metric; JLC PCB PART NUMBER C2907090
R19: 1M; R_0603_1608Metric; JLC PCB PART NUMBER C2907115
R20: 330k; R_0603_1608Metric; JLC PCB PART NUMBER C2907151
R21: 100k; R_0603_1608Metric; JLC PCB PART NUMBER C328419
R22: 0.4R; R_0603_1608Metric; JLC PCB PART NUMBER C2907088
R23, R24: 1k; R_0603_1608Metric; JLC PCB PART NUMBER C2913953
R25, R26: R_Small_US; R_0603_1608Metric
R27: R_prog; R_0603_1608Metric
RA1: RA; TestPoint_Pad_D1.0mm
RED1: LED RED; LED_0603_1608Metric; JLC PCB PART NUMBER C2917808
RL1: RL; TestPoint_Pad_D1.0mm
RST_CP1: 0-RST; TestPoint_Pad_D1.0mm
SELECT1: PTS525SM15SMTR2LFS; SW_PTS525SM15SMTR2LFS; PARTREV NA; JLC PCB PART NUMBER C221856
SW1: SW_SPDT; SW_SPDT_PCM12; JLC PCB PART NUMBER C2890358
TP1: AT_RST#; TestPoint_Pad_D1.0mm
U2: CP2102-GM; QFN50P500X500X100-29N; PARTREV 1.8; JLC PCB PART NUMBER C6568
U3: ATmega328PB-A; TQFP-32_7x7mm_P0.8mm; JLC PCB PART NUMBER C194192
U4: LM3940IMP-3.3/NOPB; SOT-223; JLC PCB PART NUMBER C140319
U5: TP4056; SOP127P600X175-9N; JLC PCB PART NUMBER C725790
U6: SSD1306; OLED-128O064D; JLC PCB PART NUMBER C2890600
Y1: 16MHZ; Crystal_SMD_0603-2Pin_6.0x3.5mm; JLC PCB PART NUMBER C112972

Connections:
3.3V: IC1.15 (FR), Q1.1 (G), Q2.1 (G), R3.1, R6.1, R12.1, R13.1, U6.6 (VBAT), U6.9 (VDD), U6.11 (BS1)
+3V3: C20.1, U3.18 (AVCC), U4.3 (VO)
+5V: R2.1, R5.2
/AT_ADC1: JP5.2 (B), U3.24 (PC1)
/AT_LOD+: JP3.2 (B), U3.25 (PC2)
/AT_LOD-: JP4.2 (B), U3.23 (PC0)
/AT_RXD: JP1.1 (A), U3.30 (PD0)
/AT_SDN#: JP6.2 (B), U3.22 (PE3)
/AT_TXD: JP2.1 (A), U3.31 (PD1)
/BATTERY +VE: C23.1, J3.1, SW1.2 (B), U5.5 (BAT)
/CP_RXD: JP2.3 (B), U2.25 (RXD)
/CP_TXD: JP1.3 (B), U2.26 (TXD)
/LA: J2.S, LA1.1, R12.2, R15.1
/LOD+: IC1.12 (LOD+), JP3.1 (A)
/LOD-: IC1.11 (LOD-), JP4.1 (A)
/OUT: C18.1, IC1.10 (OUT), JP5.1 (A), R19.1
/RA: J2.R, R13.2, R14.1, RA1.1
/REF_IN: C12.2, JP7.2 (B), U3.20 (AREF)
/REF_OUT: C19.1, IC1.8 (REFOUT), JP7.1 (A), R20.2, R21.1
/RL: J2.T, R16.1, RL1.1
/RST#: C8.2, R11.2, TP1.1, U3.29 (~RESET/PC6)
/SCL_3.3: Q1.2 (S), R3.2, U6.18 (D0/SPI_SCLK/I2C_SCK)
/SCL_5: Q1.3 (D), R2.2
/SDA_3.3: Q2.2 (S), R6.2, U6.19 (D1/SPI_SDIN/I2C_SDA), U6.20 (D2/I2C_SDA)
/SDA_5: Q2.3 (D), R5.1
/SDN#: IC1.13 (~SDN), JP6.1 (A)
/USB_D+: D2.1 (K), D+1.1, J4.A6 (D+), J4.B6 (D+), U2.4 (D+)
/USB_D-: D3.1 (K), D-1.1, J4.A7 (D-), J4.B7 (D-), U2.5 (D–)
GND: C1.2, C2.1, C3.2, C6.2, C7.2, C10.1, C11.1, C12.1, C13.2, C14.2, C20.2, C21.2, C22.2, C23.2, C24.2, D1.2 (A), D2.2 (A), D3.2 (A), DRIVE1.1, IC1.14 (AC/~DC), IC1.16 (GND_1), IC1.21 (GND_2), J1.2, J3.2, J4.A1 (GND), J4.A12 (GND), J4.B1 (GND), J4.B12 (GND), R4.2, R7.2, R8.1, R26.1, R27.1, SELECT1.2, U2.3 (GND), U2.29 (GND), U3.5 (GND), U3.21 (GND), U4.2 (GND), U5.3 (GND), U6.1 (NC), U6.8 (VSS), U6.10 (BS0), U6.12 (BS2), U6.13 (/CS), U6.29 (VLSS), U6.30 (NC)
unnamed: B_TEMP1.1, R25.2, R26.2, U5.1 (TEMP)
unnamed: C1.1, C2.2, J1.5, U2.6 (VDD)
unnamed: C4.1, U6.3 (C2N)
unnamed: C4.2, U6.2 (C2P)
unnamed: C5.1, U6.4 (C1P)
unnamed: C5.2, U6.5 (C1N)
unnamed: C6.1, U6.27 (VCOMH)
unnamed: C7.1, U6.28 (VCC)
unnamed: C8.1, JP8.2 (B)
unnamed: C10.2, IC1.18 (REFIN), R8.2, R9.2
unnamed: C11.2, IC1.17 (+VS), R9.1
unnamed: C13.1, U3.7 (XTAL1/PB6), Y1.2
unnamed: C14.1, U3.8 (XTAL2/PB7), Y1.1
unnamed: C15.1, IC1.1 (HPDRIVE)
unnamed: C15.2, IC1.20 (HPSENSE), R10.2
unnamed: C16.1, IC1.5 (RLD), R16.2
unnamed: C16.2, IC1.4 (RLDFB)
unnamed: C17.1, IC1.6 (SW), R17.2, R21.2
unnamed: C17.2, IC1.19 (IAOUT), R10.1
unnamed: C18.2, R17.1, R18.1
unnamed: C19.2, IC1.7 (OPAMP+), R18.2
unnamed: C21.1, R22.2, U4.1 (VI)
unnamed: C24.1, R23.2, R24.2, R25.1, U5.4 (VCC), U5.8 (CE)
unnamed: DRIVE1.3, U3.26 (PC3)
unnamed: GREEN1.1 (K), U5.6 (~STDBY)
unnamed: GREEN1.2 (A), R23.1
unnamed: IC1.2 (+IN), R14.2
unnamed: IC1.3 (-IN), R15.2
unnamed: IC1.9 (OPAMP-), R19.2, R20.1
unnamed: J1.3, JP1.2 (C)
unnamed: J1.4, JP2.2 (C)
unnamed: J5.1, U3.17 (PB5)
unnamed: J5.2, U3.16 (PB4)
unnamed: J5.3, U3.15 (PB3)
unnamed: J5.4, U3.14 (PB2)
unnamed: J5.5, U3.13 (PB1)
unnamed: J5.6, U3.12 (PB0)
unnamed: R1.2, RST_CP1.1, U2.9 (~RST)
unnamed: R4.1, U6.26 (IREF)
unnamed: R7.1, U2.11 (~SUSPEND)
unnamed: R24.1, RED1.2 (A)
unnamed: R27.2, U5.2 (PROG)
unnamed: RED1.1 (K), U5.7 (~CHRG)
unnamed: SELECT1.3, U3.9 (PD5)
unnamed: JP8.1 (A), U2.28 (~DTR)
VCC: C22.1, R11.1, R22.1, SW1.3 (C), U3.4 (VCC)
VIN: C3.1, D1.1 (K), J1.1, J4.A4 (VBUS), J4.A9 (VBUS), J4.B4 (VBUS), J4.B9 (VBUS), R1.1, U2.7 (REGIN), U2.8 (VBUS)

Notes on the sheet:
USB TO UART CONVERTER
INSTRUMENTATION AMPLIFIER
MICROCONTROLLER
OLED 128*64
LI-ION CHARGING
5V TO 3.3V LOGIC LEVEL CONVERTER

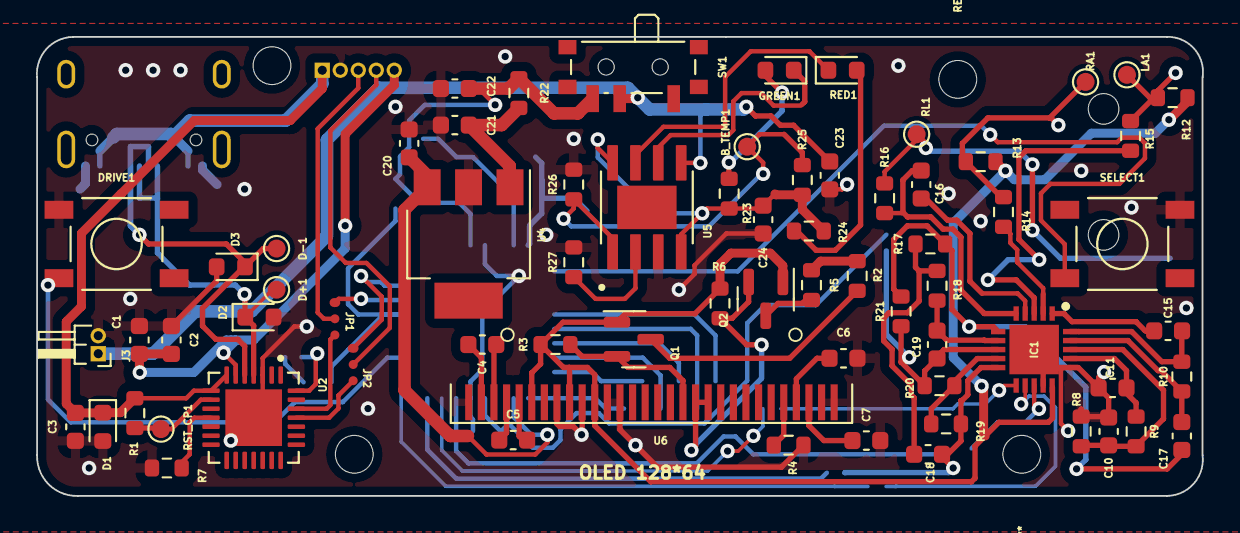
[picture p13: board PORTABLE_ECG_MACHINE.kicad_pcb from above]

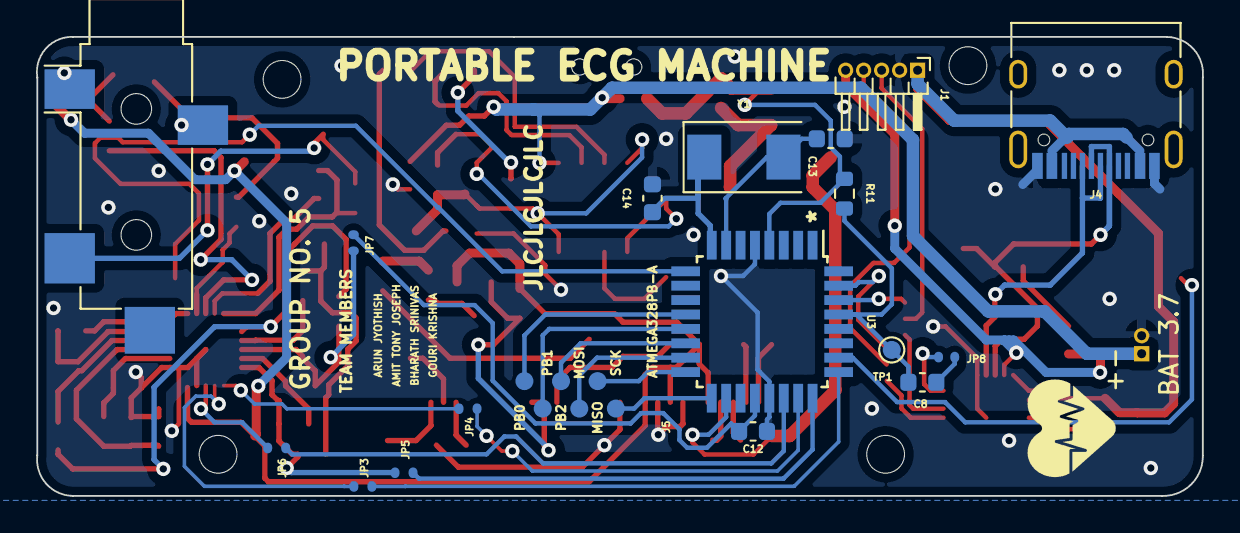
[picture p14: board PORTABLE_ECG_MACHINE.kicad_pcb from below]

Board: 2 copper layers, 64.8 x 25.5 mm, 88 parts (18 on the bottom side), 76 nets.

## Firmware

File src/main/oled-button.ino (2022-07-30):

/*
Copyright (c) by Ruebn Gaertner
2017-09-19
*/

#include <Adafruit_GFX.h>
#include <Adafruit_SSD1306.h>
#include <OneButton.h>

#define SCREEN_WIDTH 128 // OLED display width, in pixels
#define SCREEN_HEIGHT 64 // OLED display height, in pixels

#define OLED_MOSI  D1
#define OLED_CLK   D0
#define OLED_DC    D2
#define OLED_CS    D3
#define OLED_RESET D4

Adafruit_SSD1306 display(SCREEN_WIDTH, SCREEN_HEIGHT,
                         OLED_MOSI, OLED_CLK, OLED_DC, OLED_RESET, OLED_CS);

int pic = 0;
int maxPics_L1 = 5;
int maxPics_L2 = 3;

int button_brd = D5;

OneButton button(button_brd,true);

long lastmillis = 0;
long maxtime = 10000;

//#if (SSD1306_LCDHEIGHT != 64)
//#error("Height incorrect, please fix Adafruit_SSD1306.h!");
//#endif

void setup()   {
  pinMode(button_brd,INPUT_PULLUP);
button.attachClick(click);
button.attachDoubleClick(doubleclick);
button.attachLongPressStop(longPressStop);
button.attachLongPressStart(longPressStart);

display.begin(SSD1306_SWITCHCAPVCC, 0x3C);  // initialize with the I2C addr 0x3C (for the 128x64)
display.clearDisplay();
}

void loop() {
  button.tick();

//JUMP TO DEFAULT IF NO CLICK IS DETECTED
if (millis() >= (lastmillis + maxtime))
{
    pic = 0;
}

if (pic == 0)
{
  display.setTextSize(2);
  display.setTextColor(WHITE);
  display.setCursor(22,0);
  display.setCursor(0,1);
  display.print  ("Ver: 1.0.2");
  display.setTextSize(4);
  display.setCursor(  0,   21);
  display.print ("P.ECG");
  refresh();
}
//LAYER 1////////////////////////////////////////////////////
if (pic == 1)
{
  header();
  display.setCursor(0,11);  display.print (">PARAMETERS");
  display.setCursor(0,20);  display.print (" DATA RECORD");
  display.setCursor(0,29);  display.print (" DISPLAY");
  display.setCursor(0,47);  display.print (" HELP");
  display.setCursor(0,56);  display.print (" PROJECT INFO");
  refresh();
}

if (pic == 2)
{
  header();
  display.setCursor(0,11);  display.print (" PARAMETERS");
  display.setCursor(0,20);  display.print (">DATA RECORD");
  display.setCursor(0,29);  display.print (" DISPLAY");
  display.setCursor(0,47);  display.print (" HELP");
  display.setCursor(0,56);  display.print (" PROJECT INFO");
  refresh();
}

if (pic == 3)
{
  header();
  display.setCursor(0,11);  display.print (" PARAMETERS");
  display.setCursor(0,20);  display.print (" DATA RECORD");
  display.setCursor(0,29);  display.print (">DISPLAY");
  display.setCursor(0,47);  display.print (" HELP");
  display.setCursor(0,56);  display.print (" PROJECT INFO");
  refresh();
}

if (pic == 4)
{
  header();
  display.setCursor(0,11);  display.print (" PARAMETERS");
  display.setCursor(0,20);  display.print (" DATA RECORD");
  display.setCursor(0,29);  display.print (" DISPLAY");
  display.setCursor(0,47);  display.print (">HELP");
  display.setCursor(0,56);  display.print (" PROJECT INFO");
  refresh();
}

if (pic == 5)
{
  header();
  display.setCursor(0,11);  display.print (" PARAMETERS");
  display.setCursor(0,20);  display.print (" DATA RECORD");
  display.setCursor(0,29);  display.print (" DISPLAY");
  display.setCursor(0,47);  display.print (" HELP");
  display.setCursor(0,56);  display.print (">PROJECT INFO");
  refresh();
}

//LAYER 2////////////////////////////////////////////////////
if (pic == 11)
{
  header();
  display.setCursor(0,11);  display.print ("PARAMETERS");
  display.setCursor(0,20);  display.print (">UNIT:");
  display.setCursor(90,20); display.print ("none");
  display.setCursor(0,29);  display.print (" SIGNALS:");
  display.setCursor(90,29); display.print ("6");
  display.setCursor(0,38);  display.print (" DIAMETER [mm]:");
  display.setCursor(90,38); display.print ("9999");
  refresh();
}

if (pic == 21)
{
  header();
  display.setCursor(0,11);  display.print ("PARAMETERS");
  display.setCursor(0,20);  display.print (" UNIT:");
  display.setCursor(90,20); display.print ("none");
  display.setCursor(0,29);  display.print (">SIGNALS:");
  display.setCursor(90,29); display.print ("6");
  display.setCursor(0,38);  display.print (" DIAMETER [mm]:");
  display.setCursor(90,38); display.print ("9999");
  refresh();
}

if (pic == 31)
{
  header();
  display.setCursor(0,11);  display.print ("PARAMETERS");
  display.setCursor(0,20);  display.print (" UNIT:");
  display.setCursor(90,20); display.print ("none");
  display.setCursor(0,29);  display.print (" SIGNALS:");
  display.setCursor(90,29); display.print ("6");
  display.setCursor(0,38);  display.print (">DIAMETER [mm]:");
  display.setCursor(90,38); display.print ("9999");
  refresh();
}

if (pic == 12)
{
  header();
  display.setCursor(0,11);  display.print ("DATA RECORD");
  display.setCursor(0,20);  display.print ("M-CARDIAL INFR.");
  display.setCursor(0,29);  display.print ("MA.TACHYCARDIA");
  display.setCursor(0,38);  display.print ("M ISCHAEMIA");
  display.setCursor(0,47);  display.print ("VAL3");
  display.setCursor(0,56);  display.print ("VAL4");
  refresh();
}

if (pic == 13)
{
  header();
  display.setCursor(0,11);  display.print ("DISPLAY");
//  display.setCursor(0,20);  display.print ("VAL0");
//  display.setCursor(0,29);  display.print ("VAL1");
//  display.setCursor(0,38);  display.print ("VAL2");
   display.setCursor(0,20);  display.print ("M-CARDIAL INFR.");
  display.setCursor(0,29);  display.print ("MA.TACHYCARDIA");
  display.setCursor(0,38);  display.print ("M ISCHAEMIA");
  display.setCursor(0,47);  display.print ("VAL3");
  display.setCursor(0,56);  display.print ("VAL4");
  refresh();
}

if (pic == 14)
{
  header();
  display.setCursor(0,11);  display.print ("HELP");
 display.setCursor(0,20);  display.print ("Connect");
  display.setCursor(0,29);  display.print ("RA- R.Arm");
  display.setCursor(0,38);  display.print ("LA- L.Arm");
 display.setCursor(0,47);  display.print ("RL- R.Leg");
//
//
//   display.setCursor(0,20);  display.print ("M-CARDIAL INFR.");
//  display.setCursor(0,29);  display.print ("MA.TACHYCARDIA");
//  display.setCursor(0,38);  display.print ("M ISCHAEMIA");
//  display.setCursor(0,47);  display.print ("VAL3");
//  display.setCursor(0,56);  display.print ("VAL4");
  refresh();
}

if (pic == 15)
{
  header();
  display.setCursor(0,11);  display.print ("PROJECT INFO");
  display.setCursor(0,20);  display.print ("NAME: ");
  display.setCursor(50,20); display.print ("P-ECG");
  display.setCursor(0,29);  display.print ("DATE:");
  display.setCursor(50,29); display.print ("2022-JUL-7");
  display.setCursor(0,38);  display.print ("BY:");
  display.setCursor(50,38); display.print ("GROUP 05");
  refresh();
}

}

////////////////////////////////////////////////////////////////////////////////////////////////////////
void click(){
  lastmillis = millis();
  if(pic>=0 && pic<10)
  {
    if (pic >= maxPics_L1)
    {
      pic=1;
    }
    else if(pic < maxPics_L1)
    {
      pic++;
    }
  }

  if(pic>=10 && pic<100)
  {
    if (pic > 30)
    {
      pic=11;
    }
    else if (pic < 30)
    {
      pic=pic+10;
    }
  }
}

void doubleclick(){
  lastmillis = millis();
  if (pic == 11 || pic == 21 || pic == 31) pic=1;
  if (pic == 12) pic=2;
  if (pic == 13) pic=3;
  if (pic == 14) pic=4;
  if (pic == 15) pic=5;
}

void longPressStart(){
  lastmillis = millis();
  if (pic>0 & pic<10)
  {
    pic=pic+10;
  }
}

void longPressStop(){
    ;
}

void header()
{
  display.setTextSize(1);
  display.setTextColor(WHITE);
  display.setCursor(22,0);  display.print("P-ECG");
  display.drawLine (0,9,128,9, WHITE);
}

void refresh()
{
  display.display();
  delay(00);
  display.clearDisplay();
}

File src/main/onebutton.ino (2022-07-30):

/**
 * FunctionalButton.ino - Example for the OneButtonLibrary library.
 * This is a sample sketch to show how to use OneClick library functionally on ESP32,ESP8266... 

 * 
 */
#include <Arduino.h>
#include <OneButton.h>
#include <filters.h>

#define button_pin D4
int ecg_signal  = 0 ; 
unsigned long int endtime =0; 
unsigned long int starttime = 0;
String Ecg_data ="data: ";
bool flag = false;
const float cutoff_freq   = 17.0;  //Cutoff frequency in Hz
const float sampling_time = 0.007; //Sampling time in seconds.

//int count =0 ;/
IIR::ORDER  order  = IIR::ORDER::OD4; // Order (OD1 to OD4)

// Low-pass filter
Filter f(cutoff_freq, sampling_time, order);

//unsigned long int timer = millis();/

class Button{
	private:
		OneButton button;
		int value;
	public:
		explicit Button(uint8_t pin):button(pin) {
			button.attachClick([](void *scope) { ((Button *) scope)->Clicked();}, this);
		}

		void Clicked(){
			Ecg_data = "data : ";
			flag = true;
			int init_delay = 5000;
			int end_delay = 10000;
			starttime = millis() + init_delay;
			endtime= millis() + end_delay;
			Serial.print("start time: ");
			Serial.print("end time: ");
			Serial.println(starttime);
			Serial.println(endtime);
		}

		void handle(){
			button.tick();
		}
};

Button button(button_pin);

void setup() {
	pinMode(4,INPUT_PULLUP);
	Serial.begin(9600);
}

void loop() {
	button.handle();
	unsigned long int Current_time= millis();
	if (starttime < Current_time && Current_time < endtime)
	{

		int filtered_val = f.filterIn(analogRead(A0));
		Ecg_data += (String)(filtered_val) +",";
    
//    count ++;/
//		Serial.print("Count data: ");/
//		Serial.println(count);/
	}

	if ( Current_time > endtime && flag)
	{
		// push code
		Serial.println(Ecg_data);
		flag = false;
	}
	//Serial.println(Current_time);/
}

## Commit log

2022-05-17 schema update | datasheet & ref add | pcbnew initiate
    [632723300011.psm, AD8232ACPZ.stl, AD8232ACPZ.stp, PORTABLE_ECG_MACHINE.kicad_pcb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]
2022-05-17 OLED-INSTR_AMP-LION_CHAR-UART EESCHEMA UPDATE | PCBNEW ROUGH ARANGE
    [PORTABLE_ECG_MACHINE.kicad_pcb, PORTABLE_ECG_MACHINE.kicad_sch]
2022-05-17 PCBNEW ROUGH STRUCTURE | EDGECUT PR
    [PORTABLE_ECG_MACHINE.kicad_pcb, PORTABLE_ECG_MACHINE.kicad_sch]
2022-05-17 PCBNEW edgecut update| compact rough design
    [PORTABLE_ECG_MACHINE.kicad_pcb]
2022-05-17 Fill Zone add | Edgecut complete
    [PORTABLE_ECG_MACHINE.kicad_pcb]
2022-05-18 PCBNEW LAYOUT FIX | ADD LIPO-USB_CONN-AUDIO_JACK-TACTILE SWITCH
    [PORTABLE_ECG_MACHINE.kicad_pcb, PORTABLE_ECG_MACHINE.kicad_sch]
2022-05-18 DRC CHECK
    [PORTABLE_ECG_MACHINE.kicad_pcb]
2022-05-19 OLED 3D change | uC add | .step gen v4
    [PORTABLE_ECG_MACHINE.kicad_pcb, PORTABLE_ECG_MACHINE.kicad_sch]
2022-05-19 Conn complete | DRC CHECK2 | TEST INITIATE #V6#
    [PORTABLE_ECG_MACHINE.kicad_pcb, PORTABLE_ECG_MACHINE.kicad_sch]
2022-05-19 F.SILK AND B.SILK -- FONT FIX | LAYOUT FIX
    [PORTABLE_ECG_MACHINE.kicad_pcb]
2022-05-19 CUSTOM PAD ADD | ANNOTATION CONFLICT RECTIFY
    [PORTABLE_ECG_MACHINE.kicad_pcb, PORTABLE_ECG_MACHINE.kicad_sch]
2022-05-22 conn complete | solder jumper add
    pcbnew connection complete with respect to schematics, solder jumper add
    [PORTABLE_ECG_MACHINE.kicad_pcb, PORTABLE_ECG_MACHINE.kicad_sch]
2022-05-24 new revision initiate
    [PORTABLE_ECG_MACHINE.kicad_pcb]
2022-05-26 git pull stash?
    [PORTABLE_ECG_MACHINE.kicad_pcb]
2022-05-27 version 2.0 | oled 128*64
    new version created substituted 128*64 instead of 128*64. EESCHEMA and PCBNEW completed. OLED 128*64 3D MODEL need to fix
    [PORTABLE_ECG_MACHINE.kicad_pcb, PORTABLE_ECG_MACHINE.kicad_sch]
2022-06-02 BOM-README update
    [PORTABLE_ECG_MACHINE-B_Cu.gbr, PORTABLE_ECG_MACHINE-B_Mask.gbr, PORTABLE_ECG_MACHINE-B_Paste.gbr, PORTABLE_ECG_MACHINE-B_Silkscreen.gbr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]
2022-06-04 REV 3
    footprint change tp4056,add new 3d model oled 128*64,kicad render imgs add
    [PORTABLE_ECG_MACHINE.kicad_pcb, PORTABLE_ECG_MACHINE.kicad_sch]
2022-06-04 schematics update
    [PORTABLE_ECG_MACHINE.kicad_pcb, PORTABLE_ECG_MACHINE.kicad_sch]
2022-06-04 rev3 fab files, board pdf
    [PORTABLE_ECG_MACHINE-B_Cu.gbr, PORTABLE_ECG_MACHINE-B_Mask.gbr, PORTABLE_ECG_MACHINE-B_Paste.gbr, PORTABLE_ECG_MACHINE-B_Silkscreen.gbr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]
2022-06-04 rev3 modfied
    [AD8232ACPZ.stl, AD8232ACPZ.stp, LCSC_Bom_Exported_2022-06-05.csv, PORTABLE_ECG_MACHINE-B_Cu.gbr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]
